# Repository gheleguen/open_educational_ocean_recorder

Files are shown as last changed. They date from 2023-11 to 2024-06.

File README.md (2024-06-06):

# Sonde de température de fond
## 1/ Introduction
Cette sonde est un instrument permettant d'enregistrer la température de fond marin avec un précision de l'ordre du dixième de degrés Celsius. 
Elle a été conçu pour permettre un simple enregistrement de la température de l'eau en fonction du temps. 
La sonde est disigné de manière à pouvoir recevoir de nouvelles fonctions comme la mesure de la pression ou de la conductivité. 

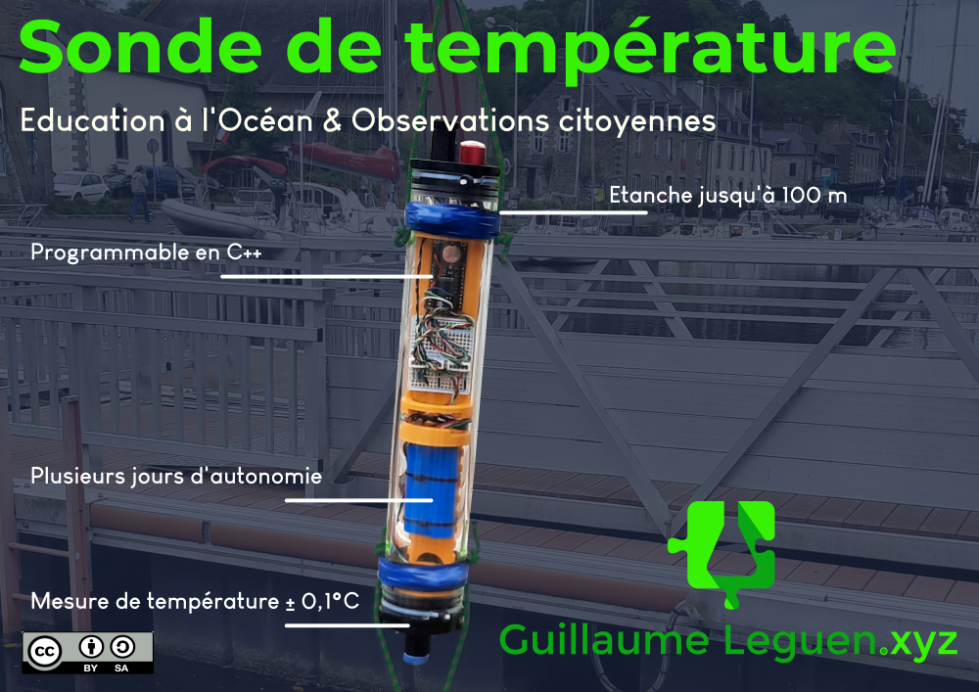
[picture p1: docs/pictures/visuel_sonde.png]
Visuel sonde de température


## 2/ Toutes les clés pour se lancer

### 2.1 Télécharger l'archive

Avant toute chose, [télécharger l'archive du projet](https://github.com/gheleguen/open_educational_ocean_recorder/archive/refs/heads/main.zip). C'est dans ce dossier que se trouve tous les fichiers de documentations mais aussi les fichiers de découpes ou les modèles d'impression 3D. 

**Ou passer par Git Hub**

Se rendre dans le [git hub](https://github.com/gheleguen/open_educational_ocean_recorder.git) et télécharger l'archive complète du projet. 

**Ou en lignes de commandes**

 - Ouvrir un terminal linux,
 - Si ce n'est pas déjà fait installer ```git``` : <pre>sudo apt install git</pre>
 - Se placer dans le dossier de votre ordinateur où vous souhaitez enregistrer l'archive.
 - Cloner l'archive : <pre>git clone https://github.com/gheleguen/open_educational_ocean_recorder.git</pre> 

### 2.2 L'arborescence de l'archive

 - **docs :** Est le dossier qui contient les documents et images qui constituent la documentation.  Ce sont des fichiers marckdown (.md) que l'on peut ouvrir avec un éditeur de texte.

 - **Hardware :** Le dossier qui contient les fichiers d'impressions 3D, de découpe laser...  

 - **Software :** Le dossier qui contient le code à flasher sur l'arduino.

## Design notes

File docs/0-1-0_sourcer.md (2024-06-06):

# A. Nomenclature / Le sourcing (V1.0)

Le sourcing est la première étape du projet et souvent la plus fastidieuse. Sourcer désigne le fait de rassembler tout ce qui sera nécéssaire pour fabriquer un objet libre. Ce projet demande des composants que l'on trouvera chez un grand-nombre de fournisseurs différents. De plus, ces fournisseurs peuvent différer en fonction du lieu et du moment où l'on va construire un instrument.

**Attention :** Veiller à effectuer ce travail préparatoire bien avant la fabrication. En effet, certaines commandes peuvent avoir de long délais. Et cela sans compter le temps nécessaire pour le travail du sourcing lui-même. 

## 1. Présentation du fichier de sourcing

 - Chercher dans le dossier "docs/files/sourcing" directement dans l'archive github, le tableur qui conviendrait à votre région ou plus proche en temps de votre date d'achat. 
 - Ouvrir le fichier de sourcing au moyen d'un tableur. Ce fichier a été créé au moyen du logiciel libre [Libre office calc](https://fr.libreoffice.org/download/telecharger-libreoffice/) mais pourra très bien être ouvert par d'autres logiciels de tableurs.

 - Ce fichier se compose d'un onglet listant tous les composants et plusieurs autres onglets dont chacun permettra au moyen d'un tableau croisé dynamique de réaliser des notes de traçabilités (ceci permettra de faciliter le travail de validation par votre administration avant l'achat):

### 1.1 Détails du tableau "Liste des éléments"

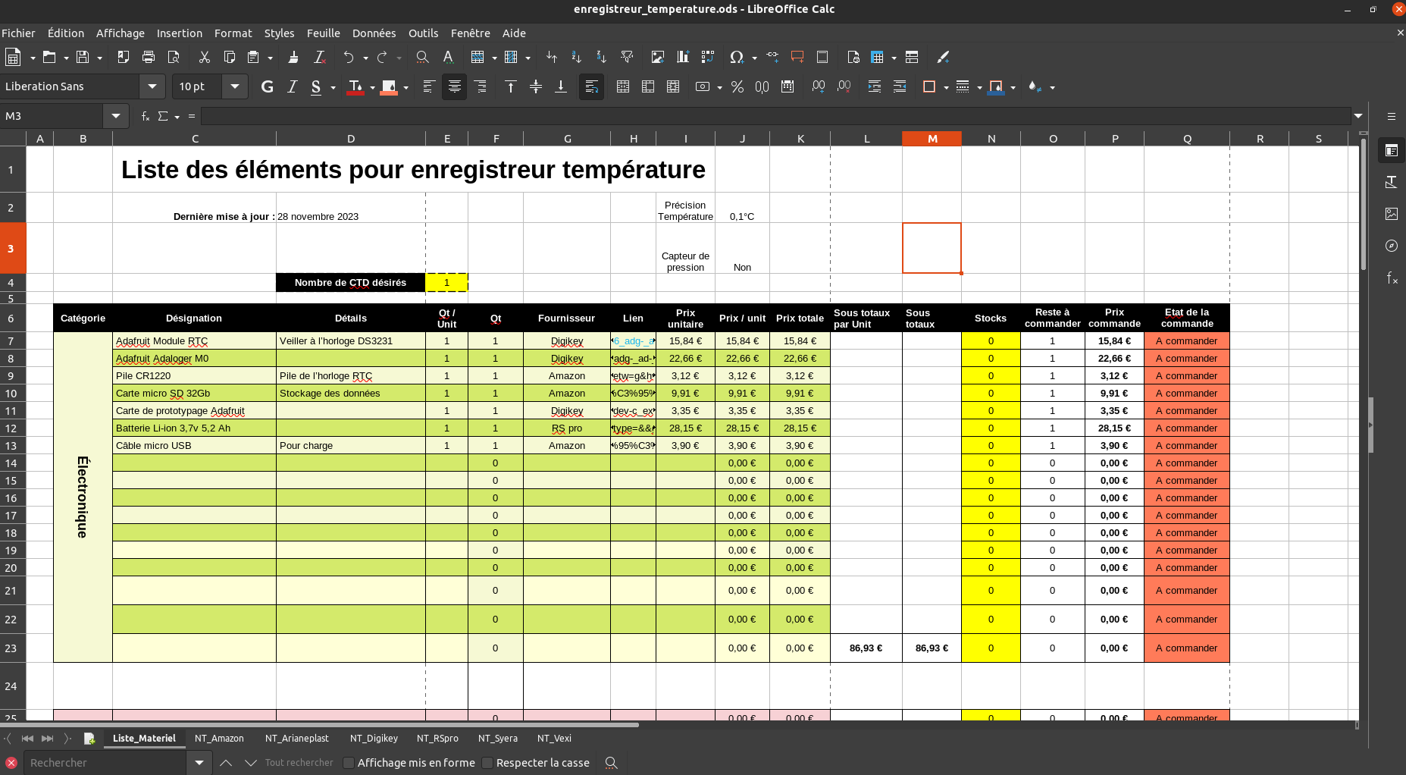
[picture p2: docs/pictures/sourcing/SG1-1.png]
SG1-1


 - **Catégorie :** Catégorie de composants (ex : Electronique, Visserie...)
 - **Désignation :** Appellation du composant
 - **Détails :** Information complémentaire, souvent des détails auquel faire attention.
 - **Qt / Unité :** Quantité pour un instrument,
 - **Qt :** Quantité nécessaire totale pour tous les instrument que l'on souhaite fabriquer,
 - **Fournisseur :** Nom du fournisseur,
 - **Lien :** Lien d'achat,
 - **Prix unitaire :** Prix d'un seul composant,
 - **Prix / Unit :** Prix des composants de même nom pour un seul instrument,
 - **Prix totale :** Prix des composants de même nom pour tous les instruments que l'on souhaite fabriquer,
 - **Stocks :** Nombre de pièces déjà en stock,
 - **Reste à commander :** Nombre de pièces qu'il reste à commander,
 - **Prix commande :** Prix total de chacun des groupes de composants qu'il reste à commander,
 - **Etat de la commande :** Cette colonne permet de sélectionner l'état de l'approvisionnement pour chacun des composant listé. Il existe 4 états : "A commander", "En attente de réception", "Reçu" et "Colis perdu"

### 1.2 Détails d'une table "note de traçabilité"

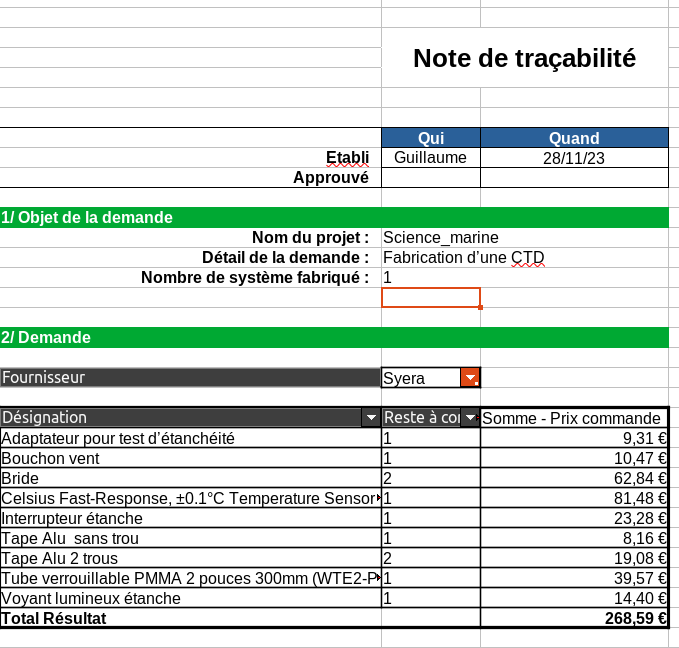
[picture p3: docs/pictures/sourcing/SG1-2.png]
SG1-2


 - Dans la seconde partie on pourra modifier au moyen d'un menu déroulant le nom du fournisseur. 
 - Le nombre de composants et les prix affichés correspondent aux quantités après déduction du stock (cf. 1.1 Détails...)
 - Noter que si la valeur renseignée dans la colonne "stocks" de la table "Liste_Materiel" est supérieure ou égale à la quantité totale nécéssaire, la quantité restante à acheter sera de 0. 

## 2. Utilisation du tableur pour sourcer

### 2.1 Mettre à jour les informations des composants

 - Se rendre dans l'onglet "Liste_Matériel"
 - Toutes les cases colorés en jaune sont à éditer en priorité : Changer le nombre d'instruments désirés et remplir la colonne des stocks (colonne"N"). Renseigner "0" si aucun composant en stock.
 - Consulter chaque lien un par un (colonne"H"), vérifier que le fournisseur convient, que le prix unitaire correspond bien à celui indiqué dans le tableau. Dans le cas contraire modifier la valeur dans la colonne "I".
 - Si le fournisseur ne distribue plus ce composant, ou que le fournisseur ne convient pas, chercher le composant ailleurs puis mettre à jour les colonnes "G" "H" et "I" avec les informations du nouveau fournisseur.
 - Surveiller ainsi ces éléments pour chacune des lignes de l'onglet "Liste_Materiel".

### 2.2 Actualiser les notes de traçabilités

 - Éditer l'entête et la partie "1/" comme désiré,
 - Pour mettre à jour la table croisée, cliquer droit sur "fournisseur" puis "actualiser",
 - Créer un onglet pour chaque fournisseur listé. 

## 3. Contribuer

Dans le cas où vous avez modifié le tableur avec des fournisseurs différents ce due au fait que vous ne résidez pas dans la même région ou pour toute autre raison, vos informations pourraient bénéficier par la suite à d'autres personnes.

**Pour contribuer**, déposez votre fichier dans le git à l'emplacement suivant "docs/files/sourcing"

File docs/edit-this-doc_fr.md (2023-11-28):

# Éditer cette documentation

## 1/ Introduction
|||
|-|-|
|Cette documentation est mise en page par ReadTheDocs.org et [lisible à l'adresse ci attaché](https://porte-a-poules.readthedocs.io/fr/latest/). En aucun cas, cette adresse permet d'éditer la documentation.|ED1-1|
|Afin de pouvoir contribuer à cette documentation, vous pouvez contribuer directement au [repository GitHub](https://github.com/gheleguen/porte_a_poules).|ED1-2|

C'est sur GitHub que sont déposés les fichiers sources. On y retrouve l'arborescence suivante : 

 - **docs :** Est le dossier qui contient les documents qui pourront être affichés sur le read the doc. Dans ce dossier sont entreposés :

   - A la racine les fichiers marckdown qui sont les textes de la documentation. Pour chaque onglet sur read the doc nous ajouterons un fichier séparé avec un titre en Anglais sans espaces terminé par "_fr" pour la version française ou "_en" pour le version anglaise. L'extention sera toujours ".md".
   - Le dossier "pictures" : Qui contient plusieurs dossiers dont chacun porte un nom en rapport avec le fichier marckdown auquel il se rapporte. Ainsi pour un fichier de doccumentation "test1_fr.md" on prendra le soin d'entreposer les images dans un dossier "/docs/pictures/test1".

 - **Hardware :** Qui est le dossier qui contient les fichiers d'impressions 3D, de découpe laser...  

Avant de faire une proposition de contribution, il est bienvenue d'éditer le repository depuis votre compte en effectuant un forke de la présente documentation. Une fois que vous aurez une version prête à être publiée il suffira de faire une pull request au "main project".
C'est un administrateur qui étudiera votre proposition pour en intégrer tout ou partie sur le projet. 

## 2/ Édition (généralités)
Ces actions peuvent se réaliser directement sur la plateforme gilhub.

### 2.1 Écriture en Marckdown
Le Marckdown est un langage de mise en forme de texte très simplifié. On peut éditer un fichier ".md" directement via gitHub ou en local de son ordinateur avec n'importe quel éditeur de texte. Cependant nous recommandons [Ghostwriter](https://ghostwriter.kde.org/fr/) qui présente l'avantage de proposer une vue en direct du rendu (aperçu HTML).

[Pour ce qui est de la syntaxe, consulter ce guide](https://www.markdownguide.org/basic-syntax/)

### 2.2 Ajout et mise à jour d'une image

#### 2.2.1 Ajout
Les images que l'on souhaite faire apparaître dans la documentation ne doivent pas être collées dans le document. 

 - Importer les images désirées que l'on aura préalablement réduites en taille chacune en dessous de 200Ko et renommées de manière à être facilement identifiables. 
 - Dans le fichier de documentation corespondant à la ligne où l'on souhaite faire apparaître l'image, ajouter la ligne suivante : 
 ```Legende_Image``` 

#### 2.2.2 Mise à jour 
Pour mettre à jour une image, il suffit de supprimer du git l'image en question et d'uploader la nouvelle image en prenant soin de renommer cette nouvelle image avec le nom exact de l'ancienne. 

## 3/ Édition du dépôt en locale (Intermédiaire)
Cette méthode permet de cloner l'archive disponible sur github sur un disque dure. Ainsi on pourra facilement modifier les différents fichiers mais aussi l'arborescence sans nécéssiter de connexion internet mais surtout cela va permettre de préparer une version qui pourra par la suite faire l'objet d'un pull request. 
Toute la démarche décrite ci-dessous est valable uniquement pour un usage depuis un ordinateur sous Linux. Il existe nécessairement des équivalent pour les autres OS mais les lignes de commandes restent les même.

### 2.1 Installer Git et préparer le terrain
 - Sur votre disque dure, définir l'espace où sera stocké le dépôt. Sachez qu'un dépôt GitHub peut peser jusq'à 500Mo. De préférence définir un dossier vide. **Attention* A ce qu'aucun dossier ou sous-dossier du chemin ne comporte de caractères spéciaux ou d'espaces. Remplacer tous les espaces par des underscore "_". 
 - Ouvrir un terminal (*Ctrl + Alt + t* sur Unbuntu).
 - Dans le cas où le paquet "git" n'est pas déjà installé sur votre PC, lancez l'installation de git :  ```sudo apt install git``` (Cette action nécessite une connexion internet).

### 2.2 Cloner le dépôt sur son disque dure
 - Ouvrir une page web avec le github que l'on souhaite cloner
 - Y copier le code "https" que l'on trouvera dans l'onglet déroulant "code" en haut à droite.
 - Dans un terminal se diriger vers l'espace prévu pour coller le dépôt. Utiliser la commande ```cd puis_chemin/de_votre_dossier```
 - Cloner le dépôt git en utilisant la commande ```git clone https://github.com/identifiant/nom_du_projet.git``` Prendre soin de remplacer l'url par celui du dépôt désiré si il est différent du notre. 
 - Le clonage va prendre quelques minutes et va coller tous les fichiers et l'arborescence dans votre répertoire.

### 2.3 Modifier le dépôt
 - Sur votre poste de travail, modifiez tous les fichiers nécessaires, déposer des fichiers, suprimez en...
 - Avant de commencer à travailler peut-être que le dépôt en ligne a été modifié depuis votre dernière mise à jour. Pour mettre à jour votre dépôt en local. Se positionner tout d'abord dans le dépôt ```cd NomduDepot``` Puis effectuer un "Pull" ```git pull```
 
### 2.4 Proposer des modifications
Si vous avez effectué des modifications, il peut-être utile de les proposer en modification au projet. Mais avant cela il peut-être utile de créer une nouvelle branche ou de faire cela depuis votre fork. 
 - Pour ajouter l'ensemble des fichiers à la liste des fichiers à commiter : ```git add *```
 - Commiter ```git commit -m "commentaire associé au commit" git@git.cru.fr:nom_projet.git nom_branche (par défaut master représentant la branche principale)```
 - Enfin pousser votre travail ```git push```

## Liens connexes
 - [Documentation Git](https://git-scm.com/about)
 - [Formation vidéo à Git](https://youtube.com/playlist?list=PLjwdMgw5TTLXuY5i7RW0QqGdW0NZntqiP)

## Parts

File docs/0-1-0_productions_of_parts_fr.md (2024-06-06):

# B. Préparation des pièces (v1.0)
## 1/ Impression des pièces en 3D

Imprimer toutes les pièces nécessaires en veillant à respecter les recommandations de remplissage des pièces extérieurs. 
 - [Les fichiers STL sont disponibles ici](https://github.com/gheleguen/open_educational_ocean_recorder/hardware/v0-1-0) .

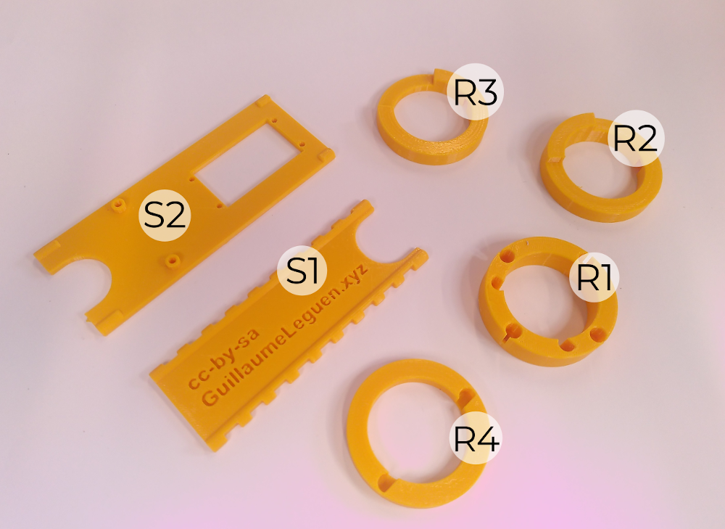
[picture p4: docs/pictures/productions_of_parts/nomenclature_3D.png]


**1.1 Pour l'intérieur du caisson :**

Il n'y a pas d'obligation quand au matériau d'impression de ces pièces. Le PET est le matériau que nous avons utilisé du fait qu’il est très facilement accessible dans le commerce. Le PLA parait à écarter tant parfois il arrive au à la sonde d'être stocké au soleil. La température si elle atteint 60° pourrait déformer des pièces en PLA. 

Le remplissage pourra être alvéolé de manière à économiser de la matière. Nous utilisons régulièrement un remplissage à 20% et une résolution de 0,2mm.

|    Visuel    |Référence|Quantité|Dénomination et usage|
|------------------------------------|------|------|-----------------|
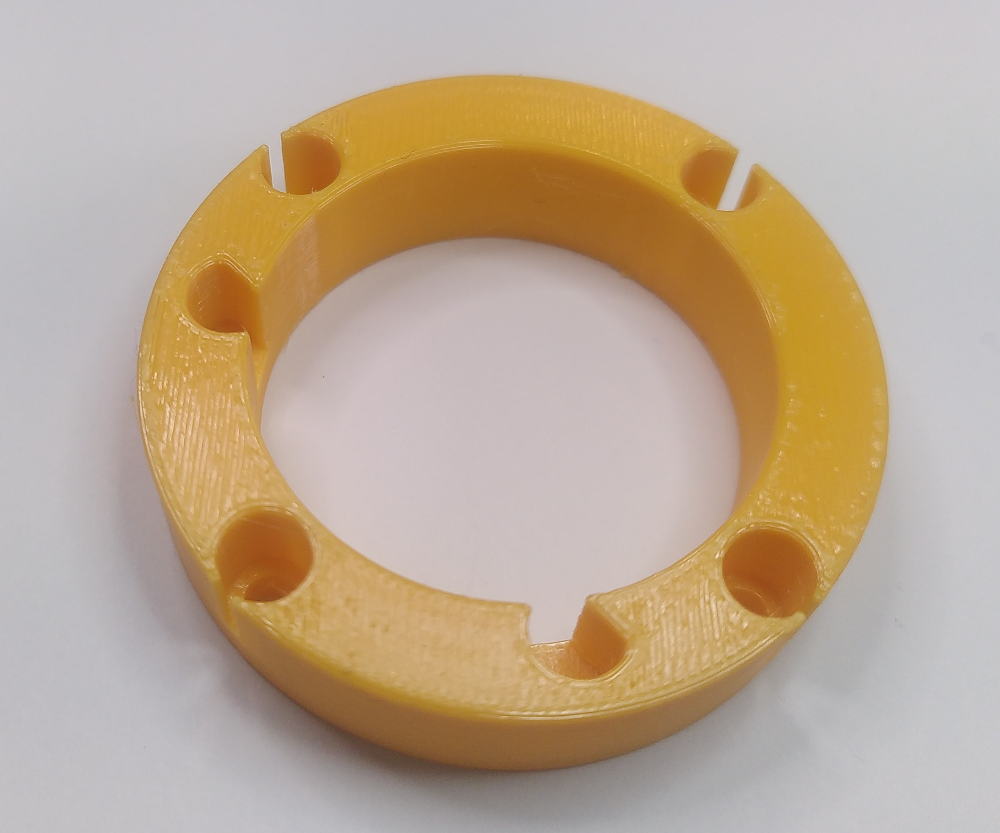
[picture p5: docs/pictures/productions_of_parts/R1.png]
POP1-1-I1
||[R1](https://github.com/gheleguen/open_educational_ocean_recorder/blob/main/hardware/v0-1-0/R1.stl)|1|Rondelle permettant de visser le support de batterie à la bride basse.|
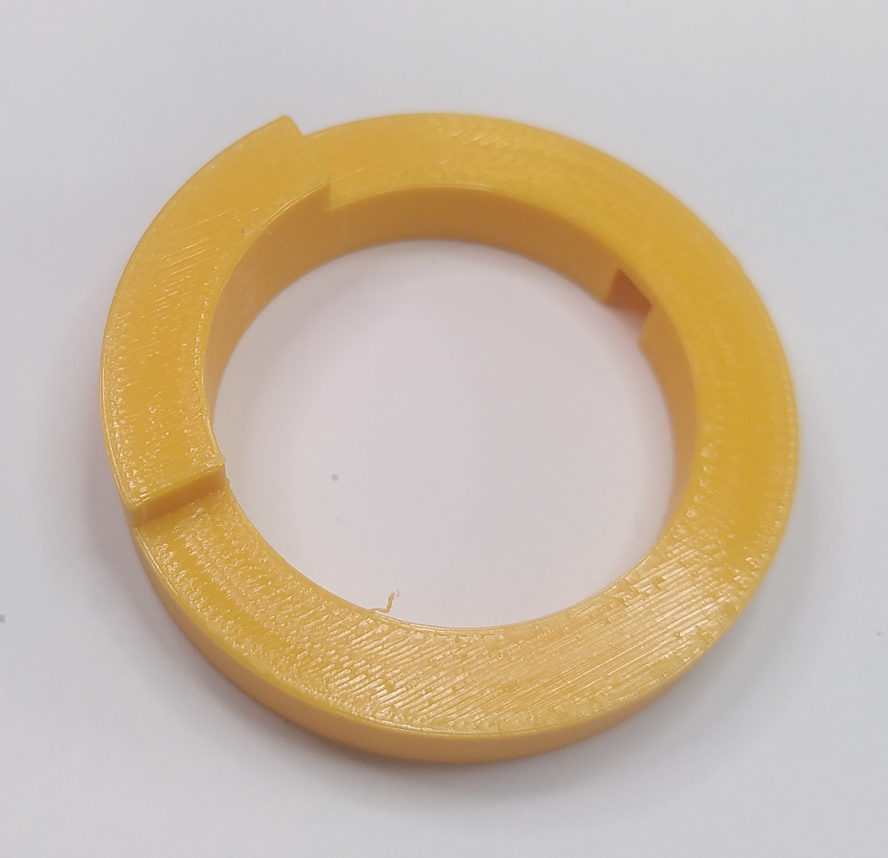
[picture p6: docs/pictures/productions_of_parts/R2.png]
POP1-1-I2
||[R2](https://github.com/gheleguen/open_educational_ocean_recorder/blob/main/hardware/v0-1-0/R2.stl)|1|Baggue haute du support de batterie. Elle est constitué d'un créneau permettant de s'imbriquer dans le support de carte électronique.|
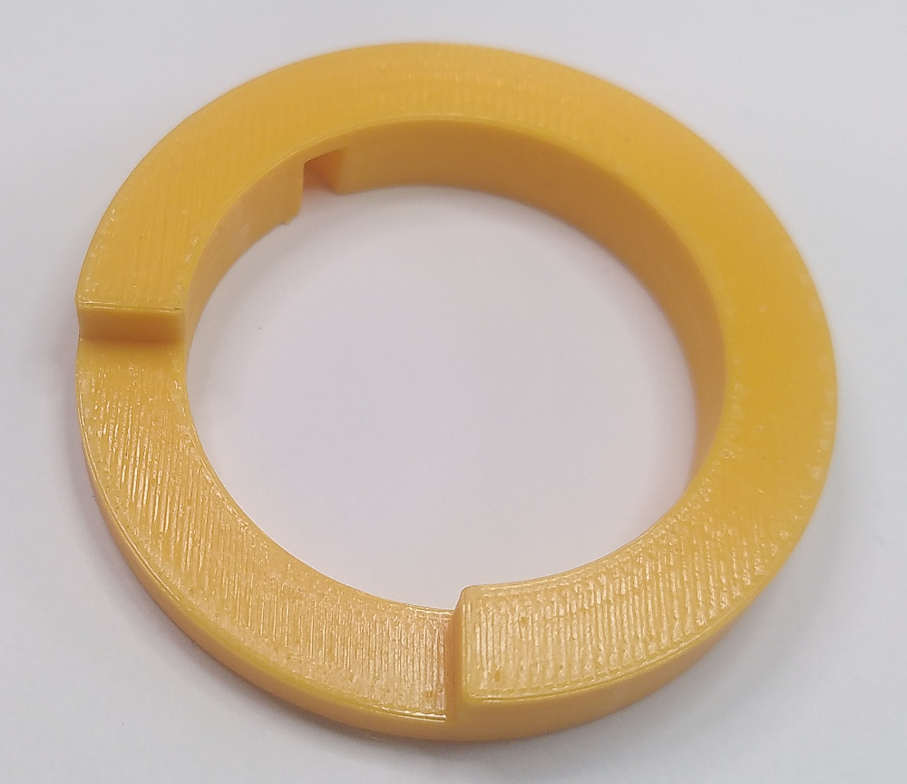
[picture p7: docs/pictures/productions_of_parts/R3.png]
POP1-1-I3
||[R3](https://github.com/gheleguen/open_educational_ocean_recorder/blob/main/hardware/v0-1-0/R3.stl)|1|Bague basse de support de carte électronique. Un creux permet de bloquer l'angle avec le support de batterie.|
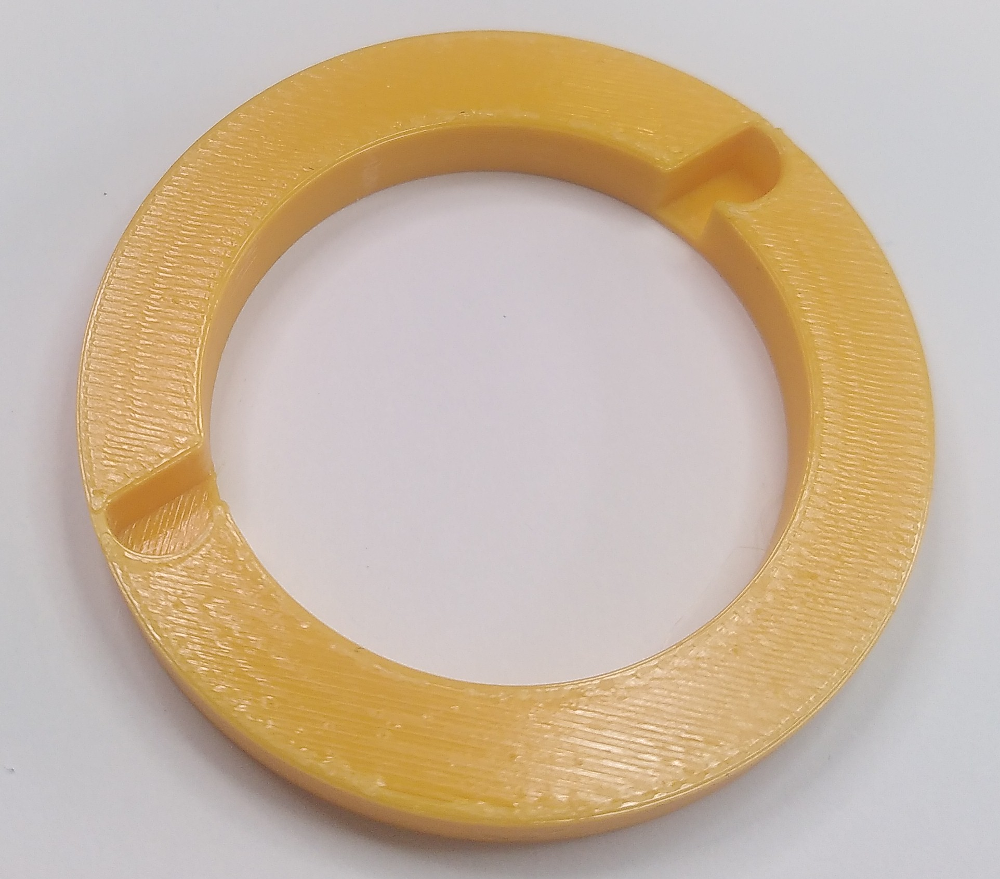
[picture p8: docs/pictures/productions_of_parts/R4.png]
||[R4](https://github.com/gheleguen/open_educational_ocean_recorder/blob/main/hardware/v0-1-0/R4.stl)|1|Bague du haut de la sonde au dessus du support des cartes électroniques|
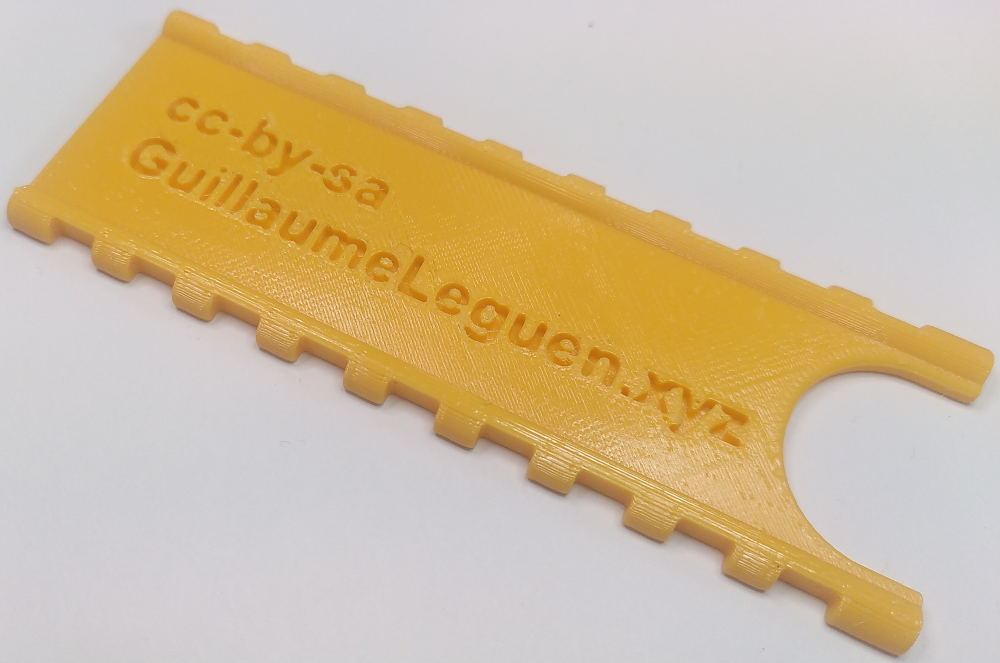
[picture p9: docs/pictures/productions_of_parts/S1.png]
||[S1](https://github.com/gheleguen/open_educational_ocean_recorder/blob/main/hardware/v0-1-0/S1.stl)|1|Support de batterie. Les créneaux permettent de fixer les batteries au moyen de colliers de serrages.|
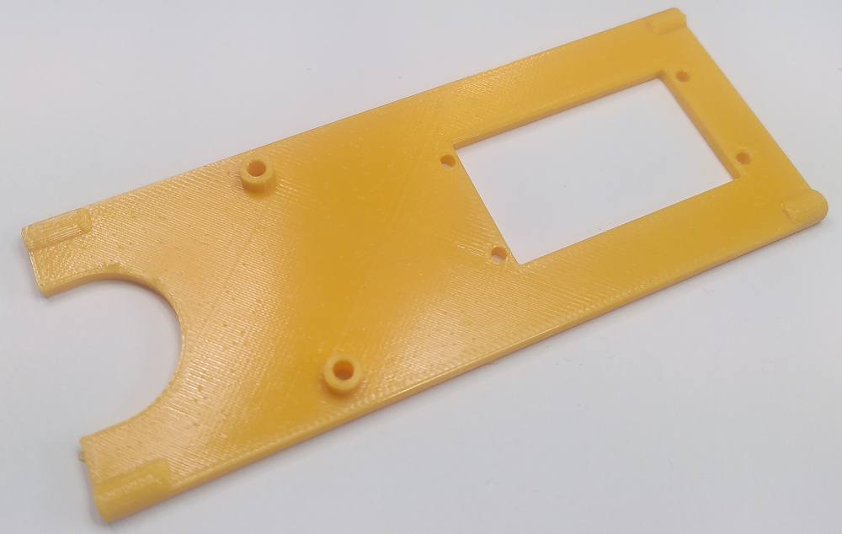
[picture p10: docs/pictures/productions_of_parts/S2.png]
||[S2](https://github.com/gheleguen/open_educational_ocean_recorder/blob/main/hardware/v0-1-0/S2.stl)|1|Support des cartes électroniques.|

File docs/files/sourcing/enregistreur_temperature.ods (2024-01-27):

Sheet: Liste_Materiel
 | Liste des éléments pour enregistreur température
 | Dernière mise à jour : | 27 janvier 2024 |  |  |  |  | Précision Température | 0,1°C
 |  |  |  |  |  |  | Capteur de pression | Non
 |  | Nombre de CTD désirés | 2
Catégorie | Désignation | Détails | Qt / Unit | Qt | Fournisseur | Lien | Prix unitaire | Prix / unit | Prix totale | Sous totaux par Unit | Sous totaux | Stocks | Reste à commander | Prix commande | Etat de la commande | Commentaire
Électronique | Adafruit Module RTC | Veiller à l’horloge DS3231 | 1 | 2 | Digikey | https://www.digikey.fr/fr/products/detail/adafruit-industries-llc/3028/5885910?productid=5885910&gad_source=1 | 15,31 € | 15,31 € | 30,62 € |  |  | 0 | 2 | 30,62 € | A commander
 | Adafruit Adaloger M0 |  | 1 | 2 | Digikey | https://www.digikey.fr/fr/products/detail/adafruit-industries-llc/2796/5804105?productid=5804105&gad_source=1 | 21,90 € | 21,90 € | 43,80 € |  |  | 0 | 2 | 43,80 € | A commander
 | Pile CR1220 | Pile de l’horloge RTC | 1 | 2 | Amazon | https://www.amazon.fr/Direct-Duracell-lithium-emball%C3%A9es-blister/dp/B005OQJCQI?adgrpid=53681020742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 | 3,12 € | 3,12 € | 6,24 € |  |  | 0 | 2 | 6,24 € | A commander
 | Carte micro SD 32Gb | Stockage des données | 1 | 2 | Amazon | https://www.amazon.fr/SANDISK-Ultra-32-SDHC-MEM/dp/B08KSY222G?__mk_fr_FR=%C3%85M%C3%85%C5%BD%C3%95%C3%91 | 6,75 € | 6,75 € | 13,50 € |  |  | 0 | 2 | 13,50 € | A commander
 | Carte de prototypage Adafruit |  | 1 | 2 | Digikey | https://www.digikey.fr/fr/products/detail/adafruit-industries-llc/1608/5154676?productid=5154676&gad_source=1 | 3,24 € | 3,24 € | 6,48 € |  |  | 0 | 2 | 6,48 € | A commander
 | Batterie Li-ion 3,7v 5,2 Ah |  | 1 | 2 | RS pro | https://fr.rs-online.com/web/p/blocs-batteries-rechargeables/1449407?matchtype=&gad_source=1&gclsrc=aw.ds | 28,15 € | 28,15 € | 56,30 € |  |  | 0 | 2 | 56,30 € | A commander
 | Câble micro USB | Pour charge | 1 | 2 | Amazon | https://www.amazon.fr/transfert-donn%C3%A9es-chargement-dappareils-compatibles/dp/B08YZ23C66?__mk_fr_FR=%C3%85M%C3%85%C5%BD%C3%95%C3%91 | 3,90 € | 3,90 € | 7,80 € |  |  | 0 | 2 | 7,80 € | A commander
 |  |  |  | 0 |  |  |  | 0,00 € | 0,00 € |  |  | 0 | 0 | 0,00 € | A commander
 |  |  |  | 0 |  |  |  | 0,00 € | 0,00 € |  |  | 0 | 0 | 0,00 € | A commander
 |  |  |  | 0 |  |  |  | 0,00 € | 0,00 € |  |  | 0 | 0 | 0,00 € | A commander
 |  |  |  | 0 |  |  |  | 0,00 € | 0,00 € |  |  | 0 | 0 | 0,00 € | A commander
 |  |  |  | 0 |  |  |  | 0,00 € | 0,00 € |  |  | 0 | 0 | 0,00 € | A commander
 |  |  |  | 0 |  |  |  | 0,00 € | 0,00 € |  |  | 0 | 0 | 0,00 € | A commander
 |  |  |  | 0 |  |  |  | 0,00 € | 0,00 € |  |  | 0 | 0 | 0,00 € | A commander
 |  |  |  | 0 |  |  |  | 0,00 € | 0,00 € |  |  | 0 | 0 | 0,00 € | A commander
 |  |  |  | 0 |  |  |  | 0,00 € | 0,00 € |  |  | 0 | 0 | 0,00 € | A commander
 |  |  |  | 0 |  |  |  | 0,00 € | 0,00 € | 82,37 € | 164,74 € | 0 | 0 | 0,00 € | A commander
Capteurs |  |  |  | 0 |  |  |  | 0,00 € | 0,00 € |  |  | 0 | 0 | 0,00 € | A commander
 | Celsius Fast-Response, ±0.1°C Temperature Sensor (I2C) |  | 1 | 2 | Syera | http://syera.fr/boutique/fr/pression-temperature/278-capteur-de-temperature.html | 81,48 € | 81,48 € | 162,96 € |  |  | 0 | 2 | 162,96 € | A commander
 |  |  |  | 0 |  |  |  | 0,00 € | 0,00 € |  |  | 0 | 0 | 0,00 € | A commander
 |  |  |  | 0 |  |  |  | 0,00 € | 0,00 € |  |  | 0 | 0 | 0,00 € | A commander
 |  |  |  | 0 |  |  |  | 0,00 € | 0,00 € | 81,48 € | 162,96 € | 0 | 0 | 0,00 € | A commander
Etanchéité | Tube verrouillable PMMA 2 pouces 300mm (WTE2-P-LOCK-TUBE-300-R1) |  | 1 | 2 | Syera | http://syera.fr/boutique/fr/tubes-2-pouces/138-tube-verrouillable-pmma-2-pouces-300mm.html | 39,57 € | 39,57 € | 79,14 € |  |  | 0 | 2 | 79,14 € | A commander
 | Bouchon vent |  | 1 | 2 | Syera | http://syera.fr/boutique/fr/accessoires-outillage/248-mise-a-l-air-libre.html?search_query=bouchon&results=48 | 10,47 € | 10,47 € | 20,94 € |  |  | 0 | 2 | 20,94 € | A commander
 | Bouchon verrouillable, aluminium 2 trous |  | 2 | 4 | Syera | http://syera.fr/boutique/fr/brides-tapes-hublots-et-domes-2-pouces/132-bouchon-verrouillable-2-trous-pour-tube-2-pouces.html?search_query=bouchon&results=48 | 37,24 € | 74,48 € | 148,96 € |  |  | 0 | 4 | 148,96 € | A commander
 | Voyant lumineux étanche |  | 1 | 2 | Syera | http://syera.fr/boutique/fr/eclairages-voyants-lasers/53-voyant-etanche-vert.html?search_query=pompe+a+vide&results=24 | 14,40 € | 14,40 € | 28,80 € |  |  | 0 | 2 | 28,80 € | A commander
 | Interrupteur étanche |  | 1 | 2 | Syera | http://syera.fr/boutique/fr/accessoires-outillage/273-interrupteur-etanche-m10-5a.html | 23,28 € | 23,28 € | 46,56 € | 162,20 € | 324,40 € | 0 | 2 | 46,56 € | A commander
Autres (*1 par groupe d’instruments) | Kit GPIO header |  | 1 | 1 | Amazon | https://www.amazon.fr/Femelle-Connecteur-Breakaway-Arduino-Prototype/dp/B093LBN495?__mk_fr_FR=%C3%85M%C3%85%C5%BD%C3%95%C3%91&sp_csd=d2lkZ2V0TmFtZT1zcF9tdGY | 13,99 € | 13,99 € | 13,99 € |  |  | 0 | 1 | 13,99 € | A commander
 | Pompe à vide | Pompe pour tester l’étanchéité des instruments | 1 | 1 | Amazon | https://www.amazon.fr/Awsuc-Manuelle-Purgeur-adaptateurs-Diagnostic/dp/B09MN36PZF?__mk_fr_FR=%C3%85M%C3%85%C5%BD%C3%95%C3%91 | 18,92 € | 18,92 € | 18,92 € |  |  | 0 | 1 | 18,92 € | A commander
 | Adaptateur pour test d’étanchéité |  | 1 | 1 | Syera | http://syera.fr/boutique/fr/accessoires-outillage/246-prise-pour-test-d-etancheite.html | 9,31 € | 9,31 € | 9,31 € |  |  | 0 | 1 | 9,31 € | A commander
 | Graisse silicone | Pour étanchéité | 1 | 1 | Amazon | https://www.amazon.fr/Xavax-Graisse-silicone-multiple-1110/dp/B00APYQTPQ?__mk_fr_FR=%C3%85M%C3%85%C5%BD%C3%95%C3%91 | 12,99 € | 12,99 € | 12,99 € |  |  | 0 | 1 | 12,99 € | A commander
 | Connectiques JST | Avec pince | 1 | 1 | Amazon | https://www.amazon.fr/connecteurs-PEBA-femelle-Adaptateur-Connecteur/dp/B07VW8F1NB?__mk_fr_FR=%C3%85M%C3%85%C5%BD%C3%95%C3%91 | 38,99 € | 38,99 € | 38,99 € |  |  | 0 | 1 | 38,99 € | A commander
 | Fils pour connectiques |  | 1 | 1 | Amazon | https://www.amazon.fr/Aussel-couleur-darc-en-ciel-1-27mm-connecteurs/dp/B077XF5LXH | 12,28 € | 12,28 € | 12,28 € |  |  | 0 | 1 | 12,28 € | A commander
 | Valise de transport H125 | /!\ Attention prendre la valise avec la mousse pré-découpé ! Valise etanche pouvant contenir 5 sondes | 1 | 1 | Vexi | https://www.vexi.fr/details/valises-plastique/etanches/valise-465-h125/ | 88,01 € | 88,01 € | 88,01 € |  |  | 0 | 1 | 88,01 € | A commander
 | Filament pour impression 3D | Choisir du PETG couleur au choix (sans copeaux de métaux) | 1 | 1 | Arianeplast | https://www.arianeplast.com/218-3d-filament-petg | 24,00 € | 24,00 € | 24,00 € | 218,49 € | 218,49 € | 0 | 1 | 24,00 € | A commander
Frais de ports | Frais de port Amazon |  | 1 | 1 | Amazon |  | 8,00 € | 8,00 € | 8,00 € |  |  | 0 | 1 | 8,00 €
 | Frais de port Arianeplast |  | 1 | 1 | Arianeplast |  | 7,00 € | 7,00 € | 7,00 € |  |  | 0 | 1 | 7,00 €
 | Frais de port Vexi |  | 1 | 1 | Vexi |  | 9,80 € | 9,80 € | 9,80 € |  |  | 0 | 1 | 9,80 €
 | Frais de port Digikey |  | 1 | 1 | Digikey |  | 18,00 € | 18,00 € | 18,00 € |  |  | 0 | 1 | 18,00 €
 | Frais de port Rspro |  | 1 | 1 | RS pro |  | 8,50 € | 8,50 € | 8,50 € |  |  | 0 | 1 | 8,50 €
 | Frais de port Syera |  | 1 | 1 | Syera |  | 11,82 € | 11,82 € | 11,82 € |  |  | 0 | 1 | 11,82 €
 |  |  |  | 1 |  |  |  | 0,00 € | 0,00 € |  |  | 0 | 1 | 0,00 €
 |  |  |  | 1 |  |  |  | 0,00 € | 0,00 € |  |  | 0 | 1 | 0,00 €
 |  |  |  | 1 |  |  |  | 0,00 € | 0,00 € |  |  | 0 | 1 | 0,00 €
 |  |  |  | 1 |  |  |  | 0,00 € | 0,00 € |  |  | 0 | 1 | 0,00 €
 |  |  |  | 1 |  |  |  | 0,00 € | 0,00 € |  |  | 0 | 1 | 0,00 €
 |  |  |  | 1 |  |  |  | 0,00 € | 0,00 € | 63,12 € | 63,12 € | 0 | 1 | 0,00 €
 |  |  |  |  |  |  |  | Total (Hors frais de ports) |  |  | 870,59 €
 |  |  |  |  |  |  |  | Total (TTC) |  |  | 933,71 € | Totale des commandes |  | 933,71 €
 |  |  |  |  | Etat
 |  |  |  |  | A commander
 |  |  |  |  | En attente de réception
 |  |  |  |  | Reçu
 |  |  |  |  | Colis perdu
 |  |  |  |  | Rien

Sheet: NT_Amazon
 | Note de traçabilité
 | Qui | Quand
Etabli |  | 27/01/24
Approuvé
1/ Objet de la demande
Nom du projet : | Science_marine
Détail de la demande : | Fabrication d’une CTD
Nombre de système fabriqué : | 2
2/ Demande
Fournisseur | Amazon
Désignation | Reste à commander | Somme - Prix commande
Câble micro USB | 2 | 7,80 €
Carte micro SD 32Gb | 2 | 13,50 €
Connectiques JST | 1 | 38,99 €
Fils pour connectiques | 1 | 12,28 €
Frais de port Amazon | 1 | 8,00 €
Graisse silicone | 1 | 12,99 €
Kit GPIO header | 1 | 13,99 €
Pile CR1220 | 2 | 6,24 €
Pompe à vide | 1 | 18,92 €
Total Résultat |  | 132,71 €

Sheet: NT_Arianeplast
 | Note de traçabilité
 | Qui | Quand
Etabli |  | 27/01/24
Approuvé
1/ Objet de la demande
Nom du projet : | Science_marine
Détail de la demande : | Fabrication d’une CTD
Nombre de système fabriqué : | 2
2/ Demande
Fournisseur | Arianeplast
Désignation | Reste à commander | Somme - Prix commande
Filament pour impression 3D | 1 | 24,00 €
Frais de port Arianeplast | 1 | 7,00 €
Total Résultat |  | 31,00 €

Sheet: NT_Digikey
 | Note de traçabilité
 | Qui | Quand
Etabli |  | 27/01/24
Approuvé
1/ Objet de la demande
Nom du projet : | Science_marine
Détail de la demande : | Fabrication d’une CTD
Nombre de système fabriqué : | 1
2/ Demande
Fournisseur | Digikey
Désignation | Reste à commander | Somme - Prix commande
Adafruit Adaloger M0 | 2 | 43,80 €
Adafruit Module RTC | 2 | 30,62 €
Carte de prototypage Adafruit | 2 | 6,48 €
Frais de port Digikey | 1 | 18,00 €
Total Résultat |  | 98,90 €

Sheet: NT_RSpro
 | Note de traçabilité
 | Qui | Quand
Etabli | Guillaume | 27/01/24
Approuvé
1/ Objet de la demande
Nom du projet : | Science_marine
Détail de la demande : | Fabrication d’une CTD
Nombre de système fabriqué : | 2
2/ Demande
Fournisseur | RS pro
Désignation | Reste à commander | Somme - Prix commande
Batterie Li-ion 3,7v 5,2 Ah | 2 | 56,30 €
Frais de port Rspro | 1 | 8,50 €
Total Résultat |  | 64,80 €

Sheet: NT_Syera
 | Note de traçabilité
 | Qui | Quand
Etabli | Guillaume | 27/01/24
Approuvé
1/ Objet de la demande
Nom du projet : | Science_marine
Détail de la demande : | Fabrication d’une CTD
Nombre de système fabriqué : | 2
2/ Demande
Fournisseur | Syera
Désignation | Reste à commander | Somme - Prix commande
Adaptateur pour test d’étanchéité | 1 | 9,31 €
Bouchon vent | 2 | 20,94 €
Bouchon verrouillable, aluminium 2 trous | 4 | 148,96 €
Celsius Fast-Response, ±0.1°C Temperature Sensor (I2C) | 2 | 162,96 €
Frais de port Syera | 1 | 11,82 €
Interrupteur étanche | 2 | 46,56 €
Tube verrouillable PMMA 2 pouces 300mm (WTE2-P-LOCK-TUBE-300-R1) | 2 | 79,14 €
Voyant lumineux étanche | 2 | 28,80 €
Total Résultat |  | 508,49 €

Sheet: NT_Vexi
 | Note de traçabilité
 | Qui | Quand
Etabli | Guillaume | 27/01/24
Approuvé
1/ Objet de la demande
Nom du projet : | Science_marine
Détail de la demande : | Fabrication d’une CTD
Nombre de système fabriqué : | 2
2/ Demande
Fournisseur | Vexi
Désignation | Reste à commander | Somme - Prix commande
Frais de port Vexi | 1 | 9,80 €
Valise de transport H125 | 1 | 88,01 €
Total Résultat |  | 97,81 €

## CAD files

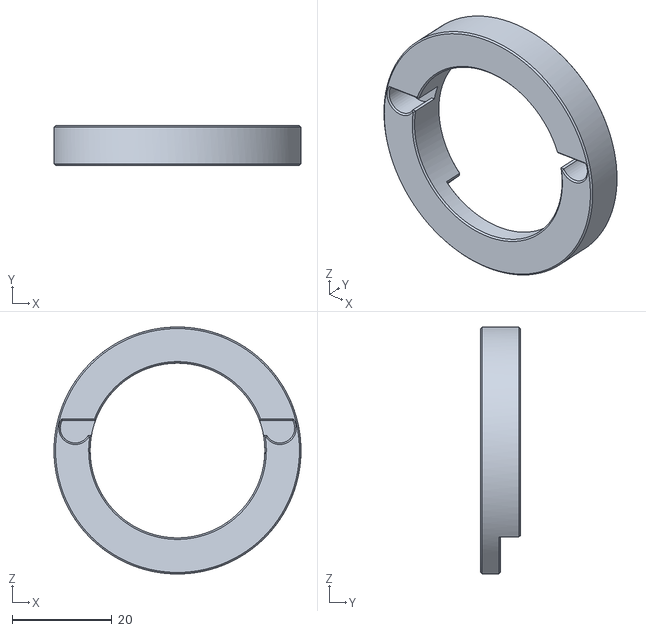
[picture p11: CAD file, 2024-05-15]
hardware/3Dprints/v0-1-0/R3.stl
49.5 x 8.00 x 49.5

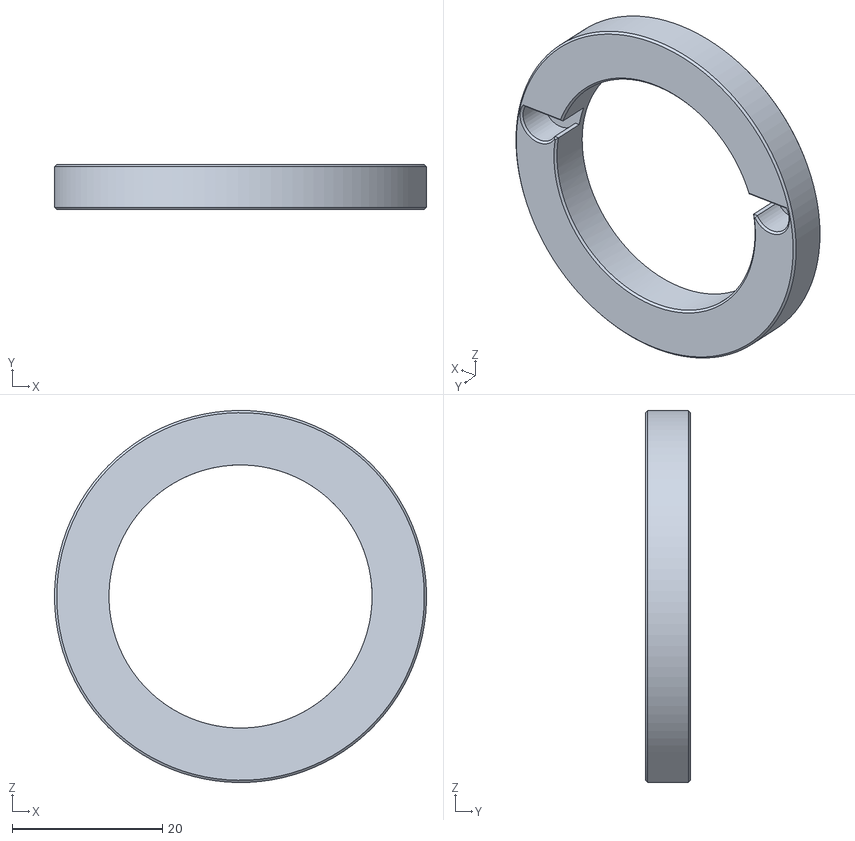
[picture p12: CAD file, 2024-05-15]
hardware/3Dprints/v0-1-0/R4.stl
49.5 x 6.00 x 49.5

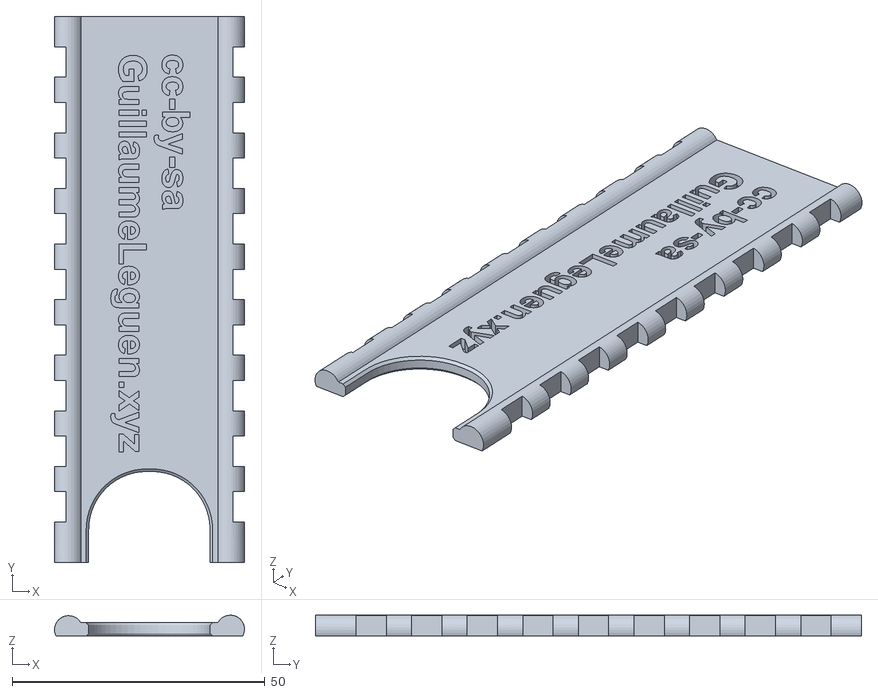
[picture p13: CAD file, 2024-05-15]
hardware/3Dprints/v0-1-0/S1.stl
37.6 x 108.0 x 4.10

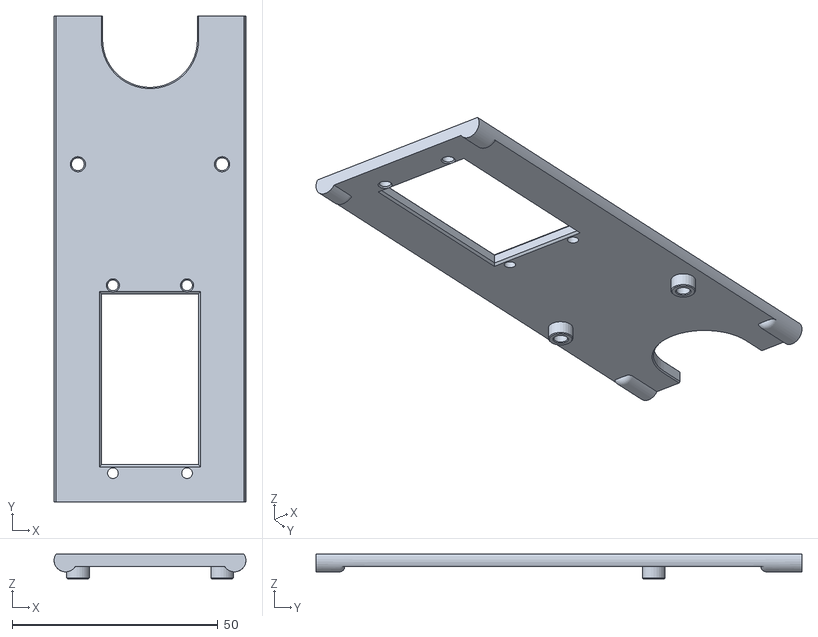
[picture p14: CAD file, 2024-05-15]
hardware/3Dprints/v0-1-0/S2.stl
46.6 x 118.0 x 6.00

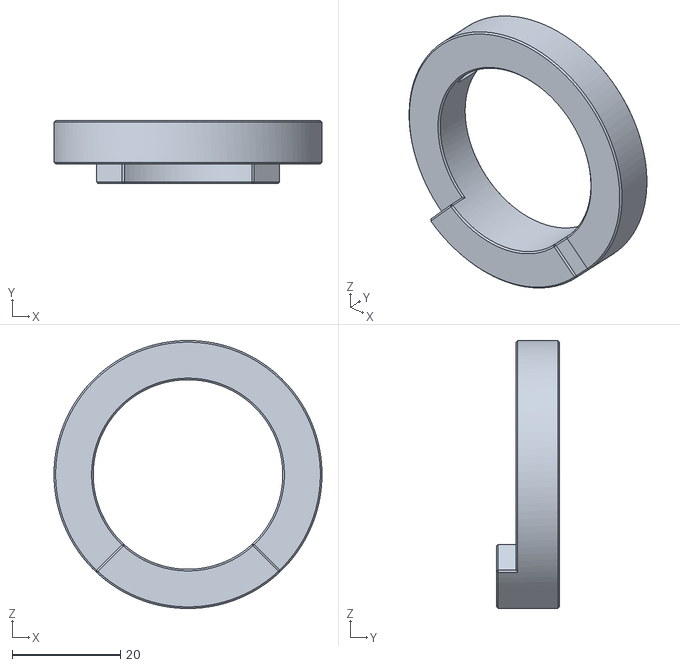
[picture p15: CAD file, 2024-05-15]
hardware/3Dprints/v0-1-0/R2.stl
49.5 x 11.6 x 49.5

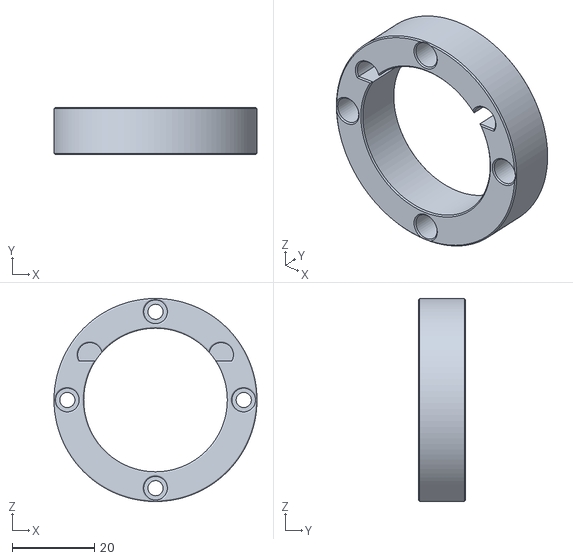
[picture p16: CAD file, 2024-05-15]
hardware/3Dprints/v0-1-0/R1.stl
49.5 x 11.5 x 49.5

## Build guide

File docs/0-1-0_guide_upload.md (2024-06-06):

# D. Guide de programmation (v1.0)
Ce présent guide détail le programme de la sonde de température. En aucun cas il n'abordera comment utiliser le logiciel Arduino IDE pour programmer une carte électronique. Pour apprendre cette manipultaion élémentaire d'arduino, sé référer à des tutoriels en lignes (mots clés : téléverser, arduino, C++).  

## 1/ Prérequis
 * [Avoir installé le logiciel Arduino IDE compatible avec votre système d'exploitation.](https://www.arduino.cc/en/software) 
 * [Avoir installé les pilotes nécéssaires pour la carte adafruit adalogger M0 sur Arduino IDE en suivant le tutoriel proposé par adafruit. ](https://learn.adafruit.com/adafruit-feather-m0-adalogger/setup)
 * Avoir installé les librairies :
   * [Wire](https://www.arduino.cc/reference/en/language/functions/communication/wire/)
   * [RTClib](https://www.arduino.cc/reference/en/libraries/rtclib/)
   * [TSYS01](https://github.com/bluerobotics/BlueRobotics_TSYS01_Library.git) (Librairie pour le capteur de température Blue robotics)
   * [SPI](https://www.arduino.cc/reference/en/language/functions/communication/spi/)
   * [SD](https://www.arduino.cc/reference/en/libraries/sd/)

## 2/ Programme
Le programme (Software) de la sonde de température est disponible dans l'archive au chemin suivant : ```/software/0-1-0_software_temp/0-1-0_software_temp.ino.```

 * [Télécharger le programme au format .ino](https://github.com/gheleguen/open_educational_ocean_recorder/blob/main/software/0-1-0_software_temp/0-1-0_software_temp.ino)

### 2.1 Détail du programme
<section style="border: 2px solid red; padding: 20px; border-radius:20px; color: red;">
Attention ! Le détail du programme ci-dessous ne reprend pas toutes les lignes du code. Pour programmer la sonde, préférez télécharger le fichier présent dans l'archive. </section>

#### 2.1.1 Les variables paramétrables

Dans cette section, il est possible de modifier les variables de temps. La sonde est programmé pour réaliser une série de mesures à intervalles réguliers. Tel que :

            M1 M2 M3 - - -Mn            M1 M2 M3 - - -Mn            M1 M2 M3 - - -Mn

 - L’intervalle entre deux séries de mesures est représenté par la variable **"delay_read_temp"**
 - Le nombre de répétitions pour chacune des séquences de prises de mesures **"repetition_mesures"**
 - L’intervalle entre chacune des répétition est défini par la variable : **"repetition_mesures"**

```c++
int delay_read_temp = 10000 ; // Temps entre chacune des série de prises de mesures
int repetition_mesures = 5 ; // Nombre de Répétitions de prises de mesures
int delay_repetition_temp = 10 ; // Temps entre chacune des répétitions
```

Ici on appel les librairies nécessaires pour l'éxecution du programme : 

```c++
//Fonctions d'appel de librairies (I2C et Wire) pour l'horloge RTC DS3231
#include <Wire.h>
#include "RTClib.h"

//Librairie pour lire le capteur de température
#include "TSYS01.h"

//Périphérique de série et la Librairie de la carte SD
#include <SPI.h> //serial peripheral interface for SD card reader
#include <SD.h> //library for SD card reader
```

Quelques variables de branchements qu'il pourrait-être nécessaire de modifier si vous n'utilisez pas tout à fait le même matériel.
```c++
// Définition des variables
float temp;
const int chipSelect = 4; //Broche de lecture du RTC
char datalogFileName[25];
char dateTimeString[40];
int Date2;
int x ;  delay(5000);
pinMode(led, OUTPUT);
int led = 6; // Broche du voyant lumineux
```

#### 2.1.2 Initialisation

Le moniteur série devra être réglé sur 9600 pour permettre la lecture lorsque la carte Arduino sera connecté au PC en USB. 
```c++
  Serial.begin(9600);
```

Initialisation de la carte SD. Dans le cas où la carte serait introuvable, aucun fichier ne sera créé et aucune mesure ne sera prise. 
```c++
  //Initialisation de la carte SD
  Serial.println("Initialisation de la carte SD...");

  if (!SD.begin(chipSelect)) {
    Serial.println("Erreur de lecture de carte SD, ou carte non présente.");
    while (1);
  }
  Serial.println("Carte SD initialisé.");

  /* Cette fonction permet à la bibliothèque SD de définir les dates correctes de création et de modification des fichiers pour tous les fichiers de la carte SD.
  SdFile::dateTimeCallback(SDCardDateTimeCallback);*/
  digitalWrite(led, HIGH);   // LED allumé
  delay(1000);
```

Ici, on teste l'horloge RTC. Puis on l'initialise. Dans le cas où la RTC aurai perdu l'heure, et sera automatiquement réglé sur l'heure de l'ordinateur qui l'a programmé. 
```c++
  //Essai de la lecture du RTC. Si l'horloge est introuvable le programme ne pourra se dérouler. 
  if (! rtc.begin()) {
    Serial.println("Erreur, RTC introuvable.");
    while (1);
  }
  
  //Initialisation de l'horloge RTC sur l'heure de l'ordinateur au téléversement.
  if (rtc.lostPower()) {

    //reset RTC with time when code was compiled if RTC loses power
    Serial.println("RTC lost power, lets set the time!");
    rtc.adjust(DateTime(F(__DATE__), F(__TIME__)));
  }
  get_numbered_filename(datalogFileName,"LOG" , "CSV");
```

Initialisation de fichier de stockage de données sur la carte SD. Certaines fonctions appel à des sous-fonctions qui seront détaillés plus bas. 
```c++
  // Initialisation du fichier de données LOG en .csv
  Serial.print("Ecriture dans le datalog: ");
  Serial.println(datalogFileName);

  File dataFile = SD.open(datalogFileName, FILE_WRITE);
  delay(250); 

  if (dataFile) {
    Serial.println("====================================================");
    Serial.println("Date,Time [UTC],Temp [°C]");
    dataFile.println("Date,Time [UTC],Temp [°C]");
    dataFile.close();

  }
  // Si le datalog ne peut-être ouvert, un message d'erreur s'affichera sur le moniteur série.
  else {
    Serial.println("Erreur: Impossible d'ouvrir le datalog");
  }

  Serial.println("Starting mesurements");
  Wire.begin();

  sensor.init();
  digitalWrite(led, LOW);   // LEd etteinte
}
```

#### 2.1.3 Boucle

Au début de la boucle on initialise la variable "x" à 0. Cette variable permet de compter le nombre de mesures de reproductions pour chacune des phases.
```c++
  x=0;
```

Tant que le nombre de répétitions de mesures n'est pas atteinte, le programme reproduit une mesure.
```c++
  while (x < repetition_mesures){
    digitalWrite(led, HIGH);   // LEd allumé
    DateTime now = rtc.now(); //check RTC
    get_date_time_string(dateTimeString, now);
    temp = sensor.temperature();

    // Lecture de la température
    sensor.read();

    // Ecriture des données sur le moniteur série
    Serial.print(dateTimeString);
    Serial.print(",");
    Serial.println(temp);
  
    //Stockage de la donnée dans le fichier de données
    File dataFile = SD.open(datalogFileName, FILE_WRITE);
    if (dataFile) {
      dataFile.print(dateTimeString);
      dataFile.print(",");
      dataFile.println(temp);
      dataFile.close();
      x = x+1;
      delay(delay_repetition_temp); // Attente entre chacune des mesures de répétition
    }
  }
```

La LED s'allume à chacune des prise de mesure de température. 
```c++
  digitalWrite(led, LOW);   // LEd etteinte
```

Cette fonction permet d'attendre le temps nécessaire avant de reproduire une séquence de mesure.
```c++
  delay(delay_read_temp); // Attente avant nouvelle séquence de mesures
```

#### 2.1.4 Fonctions secondaires

Fonction permettant le nommage du fichier de données. Elle utilise les données de date et d'heure. 
```c++
void get_numbered_filename(char* outStr, char* filePrefix, char* fileExtension) {

  //sprintf(outStr, "%s000.%s", filePrefix, fileExtension);
  DateTime now = rtc.now();
  Date2 = now.year()-2000;
  sprintf(outStr,"%02d%02d%02d00.%s",Date2,now.month(),now.day(),fileExtension); 
  int namelength = strlen(outStr);
  if (namelength > 12) Serial.println("Erreur: Nom de fichier trop long. Réduire votre nom de fichier à moins de 5 caractères (12 caractères maximum en incluant l'extension) !");

  int i = 1;
  while (SD.exists(outStr)) { 

    int hundreds = i / 100;
    outStr[namelength - 6] = '0' + (i / 10) - (hundreds * 10);
    outStr[namelength - 5] = '0' + i % 10;
    i++;
  }
}
```

Fonction d'écriture de l'heure et de la date sur chaque ligne du tableau.
```c++

void get_date_time_string(char* outStr, DateTime date) {
  sprintf(outStr, "%02d/%02d/%02d,%02d:%02d:%02d", date.year(), date.month(), date.day(), date.hour(), date.minute(), date.second());
  // Note: If you would like the date & time to be seperate columns change the space in the formatting string to a comma - this works because the file type is CSV (Comma Seperated Values)
}
```

### 2.2 Programme complet

En date du : 06/06/2024

```c++
/*
 * Ce programme écrit en C++ est destiné à une sonde de température de fond réalisé par Guillaume Leguen (guillaumeleguen.xyz).
 * Retrouvez la totalité du projet sur readthe doc : https://open-educational-ocean-recorder.readthedocs.io/fr/latest/
 * 
 * Licence : open_educational_ocean_recorder est un projet de Guillaume Leguen proposé sous licence CC-by-sa 4.0
 * Ce programme est basé en partie sur le travail d'oceanography for everyone (https://oceanographyforeveryone.com/)
*/

// Les paramétres suivant peuvent être modifiés comme réglage de la sonde
int delay_read_temp = 10000 ; // Temps entre chacune des série de prises de mesures
int repetition_mesures = 5 ; // Nombre de Répétitions de prises de mesures
int delay_repetition_temp = 10 ; // Temps entre chacune des répétitions

//Fonction d'appel de librairies (I2C et Wire) pour l'horloge RTC DS3231
#include <Wire.h>
#include "RTClib.h"

//Librairie pour lire le capteur de température
#include "TSYS01.h"

//Périphérique de série et la Librairie de la carte SD
#include <SPI.h> //serial peripheral interface for SD card reader
#include <SD.h> //library for SD card reader

TSYS01 sensor;
RTC_DS3231 rtc; // Commenter si utilisation de l'autre RTC
//RTC_PCF8523 rtc; //Décommenter si utilisation de ce RTC

// Définition des variables
float temp;
const int chipSelect = 4; //Broche de lecture du RTC
char datalogFileName[25];
char dateTimeString[40];
int Date2;
int x ;
int led = 6; // Brche du voyant lumineux

// Actions d'initialisation
void setup() {

  Serial.begin(9600);
  delay(5000);
  pinMode(led, OUTPUT);
  //Initialisation de la carte SD
  Serial.println("Initialisation de la carte SD...");

  if (!SD.begin(chipSelect)) {
    Serial.println("Erreur de lecture de carte SD, ou carte non présente.");
    while (1);
  }
  Serial.println("Carte SD initialisé.");

  /* Cette fonction permet à la bibliothèque SD de définir les dates correctes de création et de modification des fichiers pour tous les fichiers de la carte SD.
  SdFile::dateTimeCallback(SDCardDateTimeCallback);*/
  digitalWrite(led, HIGH);   // LED allumé
  delay(1000);

  //Essai de la lecture du RTC. Si l'horloge est introuvable le programme ne pourra se dérouler. 
  if (! rtc.begin()) {
    Serial.println("Erreur, RTC introuvable.");
    while (1);
  }
  
  //Initialisation de l'horloge RTC sur l'heure de l'ordinateur au téléversement.
  if (rtc.lostPower()) {

    //reset RTC with time when code was compiled if RTC loses power
    Serial.println("RTC lost power, lets set the time!");
    rtc.adjust(DateTime(F(__DATE__), F(__TIME__)));
  }
  get_numbered_filename(datalogFileName,"LOG" , "CSV");

  // Initialisation du fichier de données LOG en .csv
  Serial.print("Ecriture dans le datalog: ");
  Serial.println(datalogFileName);

  File dataFile = SD.open(datalogFileName, FILE_WRITE);
  delay(250); 

  if (dataFile) {
    Serial.println("====================================================");
    Serial.println("Date,Time [UTC],Temp [°C]");
    dataFile.println("Date,Time [UTC],Temp [°C]");
    dataFile.close();

  }
  // Si le datalog ne peut-être ouvert, un message d'erreur s'affichera sur le moniteur série.
  else {
    Serial.println("Erreur: Impossible d'ouvrir le datalog");
  }

  Serial.println("Starting mesurements");
  Wire.begin();

  sensor.init();
  digitalWrite(led, LOW);   // LEd etteinte
}

// Début du programme en boucle
void loop() {
  x=0;

  // Tant que le nombre de répétition de mesure n'est pas atteinte, le programme reproduit une mesure
  while (x < repetition_mesures){
    digitalWrite(led, HIGH);   // LEd allumé
    DateTime now = rtc.now(); //check RTC
    get_date_time_string(dateTimeString, now);
    temp = sensor.temperature();

    // Lecture de la température
    sensor.read();

    // Ecriture des données sur le moniteur série
    Serial.print(dateTimeString);
    Serial.print(",");
    Serial.println(temp);
  
    //Stockage de la donnée dans le fichier de données
    File dataFile = SD.open(datalogFileName, FILE_WRITE);
    if (dataFile) {
      dataFile.print(dateTimeString);
      dataFile.print(",");
      dataFile.println(temp);
      dataFile.close();
      x = x+1;
      delay(delay_repetition_temp); // Attente entre chacune des mesures de répétition
    }
  }
  digitalWrite(led, LOW);   // LEd etteinte
  delay(delay_read_temp); // Attente avant nouvelle séquence de mesures

}

// Fonction de nommage du fichier de données.
void get_numbered_filename(char* outStr, char* filePrefix, char* fileExtension) {

  //sprintf(outStr, "%s000.%s", filePrefix, fileExtension);
  DateTime now = rtc.now();
  Date2 = now.year()-2000;
  sprintf(outStr,"%02d%02d%02d00.%s",Date2,now.month(),now.day(),fileExtension); 
  int namelength = strlen(outStr);
  if (namelength > 12) Serial.println("Erreur: Nom de fichier trop long. Réduire votre nom de fichier à moins de 5 caractères (12 caractères maximum en incluant l'extension) !");

  int i = 1;
  while (SD.exists(outStr)) { 

    int hundreds = i / 100;
    outStr[namelength - 6] = '0' + (i / 10) - (hundreds * 10);
    outStr[namelength - 5] = '0' + i % 10;
    i++;

  }

}

// Fonction d'écriture de l'heure et de la date.
void get_date_time_string(char* outStr, DateTime date) {
  sprintf(outStr, "%02d/%02d/%02d,%02d:%02d:%02d", date.year(), date.month(), date.day(), date.hour(), date.minute(), date.second());
  // Note: If you would like the date & time to be seperate columns change the space in the formatting string to a comma - this works because the file type is CSV (Comma Seperated Values)
}

// Fonction permettant à la bibliothèque SD de définir les dates correctes de création et de modification des fichiers pour tous les fichiers de la carte SD 
void SDCardDateTimeCallback(uint16_t* date, uint16_t* time)
{
  DateTime now = rtc.now();
  *date = FAT_DATE(now.year(), now.month(), now.day());
  *time = FAT_TIME(now.hour(), now.minute(), now.second());
}
```

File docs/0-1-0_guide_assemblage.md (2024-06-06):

# C. Guide d'assemblage (v1.0)
Ce présent guide d'assemblage, suppose que vous ayez réalisés les étapes précédentes et nottamment l'étape du sourcing. Vérifiez avoir reçu tous les composants avant de commencer. 
Avant de réaliser le montage de la sonde, il peut-être utile de vérifier le bon fonctionnement des capteurs. Pour cela suivez les protocoles de tests disponibles en Annexes de ce chapitre. 
 - [Tester le capteur de temprérature](0-0-1_test_temp-sensor.md)
 - [Tester l'horloge RTC](0-0-1_test_set_rtc-ds3231.md)

## 1/ Préparations, câblages et soudures
### 1.1 Connectique du capteur de température

 - Rassembler le capteur de température (et ses accessoires, le joint et l'écrou), un bloc connectique mâle JST 4 voies (4P Plug Housing), 4 ferrures mâles JST à sertir, ainsi qu'une bride à 2 perforations (ou une plaque alu deux perforations). 
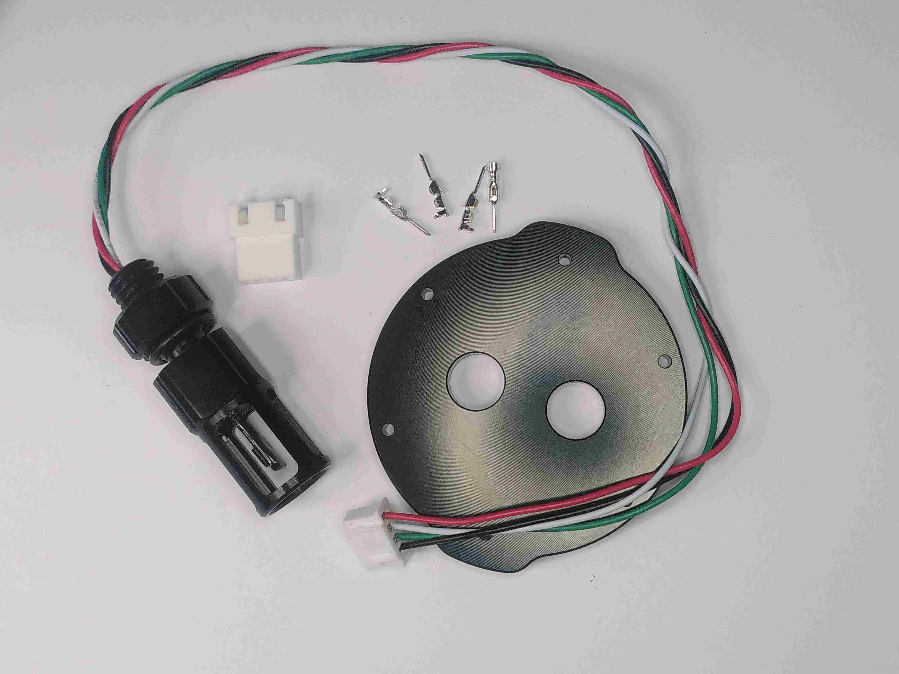
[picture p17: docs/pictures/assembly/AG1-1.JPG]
Photo montrant les éléments nécessaires

 - A l'aide d'une pince coupante, sectionner le connecteur du capteur déjà en place. Veiller à couper au plus proche du connecteur afin de conserver un maximum de fil.
 - Dénuder chacun des fils au moyen d'une pince à dénuder. 
 - Sertir au bout de chaque fil une ferrure mâle.

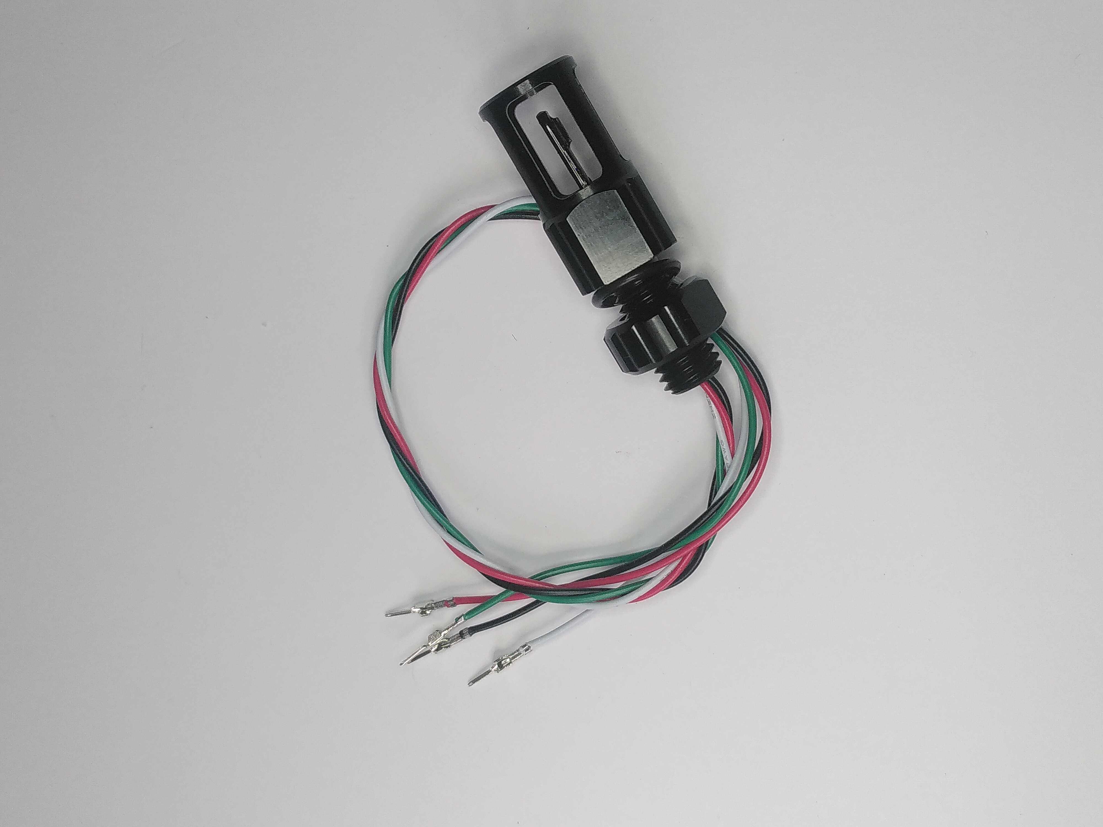
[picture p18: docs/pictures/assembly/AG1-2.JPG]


<section style="border: 2px solid red; padding: 20px; border-radius:20px; color: red;">
Attention ! Avant de positionner les ferrures dans le bloc connecteur JST, il faudra passer le capteur dans un trou de la bride. Ceci ne pouvant pas être fait après car le connecteur ne passe pas dans la perforation de la bride. </section>

 - Positionner le joint torique du coté extérieur, puis passer le pénétrateur dans la bride, pour enfin serrer avec l'écrou à la main puis à l'aide d'une clé. 

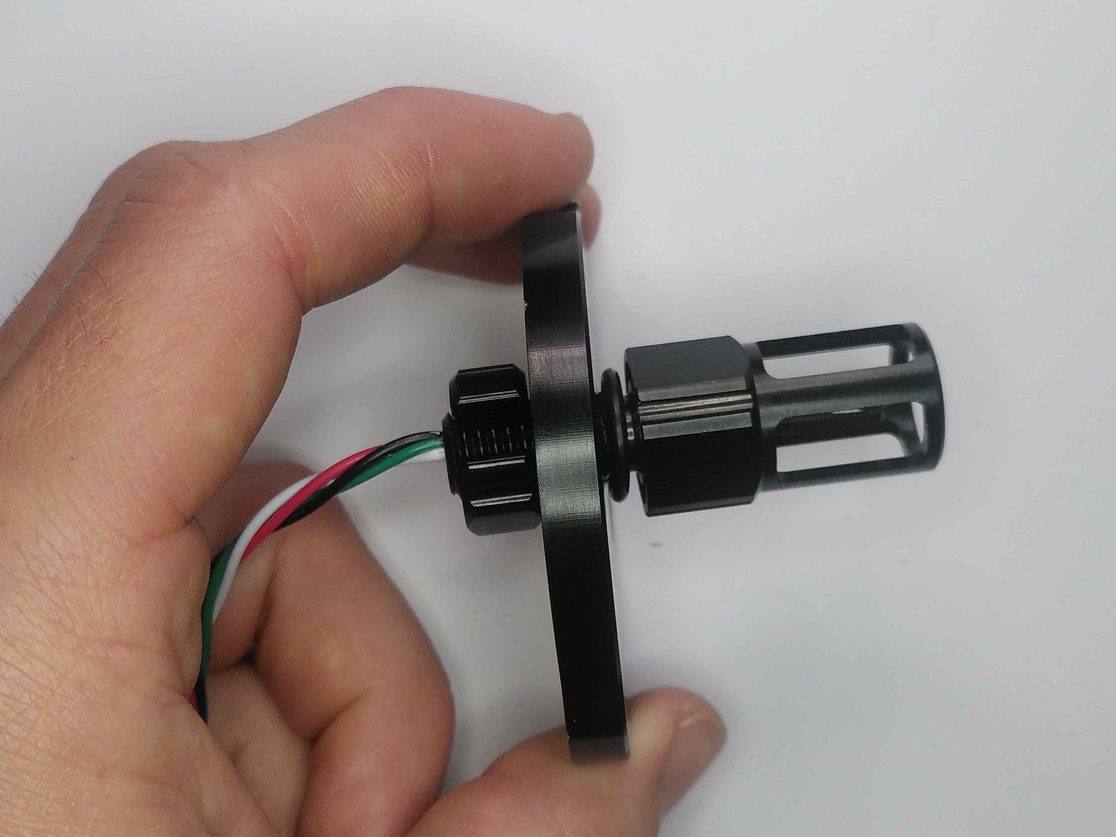
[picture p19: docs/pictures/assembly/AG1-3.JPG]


 - Enfoncer chacun des fil dans le connecteur JST. En suivant le schéma ci-dessous. 

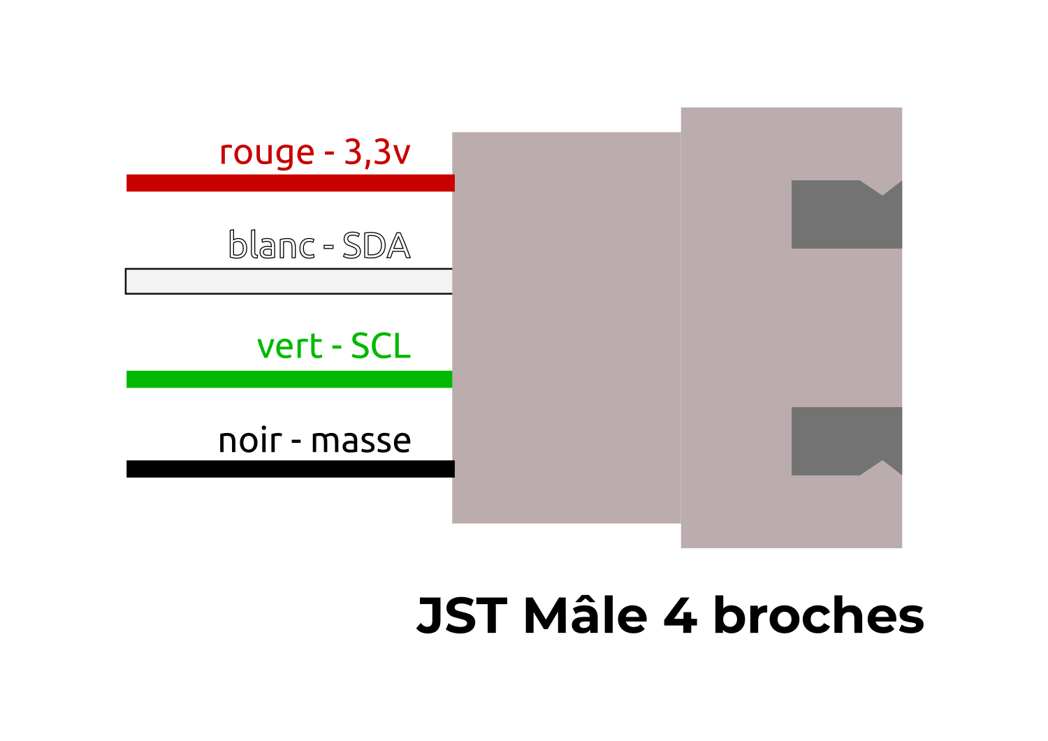
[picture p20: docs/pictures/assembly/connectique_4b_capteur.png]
Schèma d'implantation des fils du capteur.

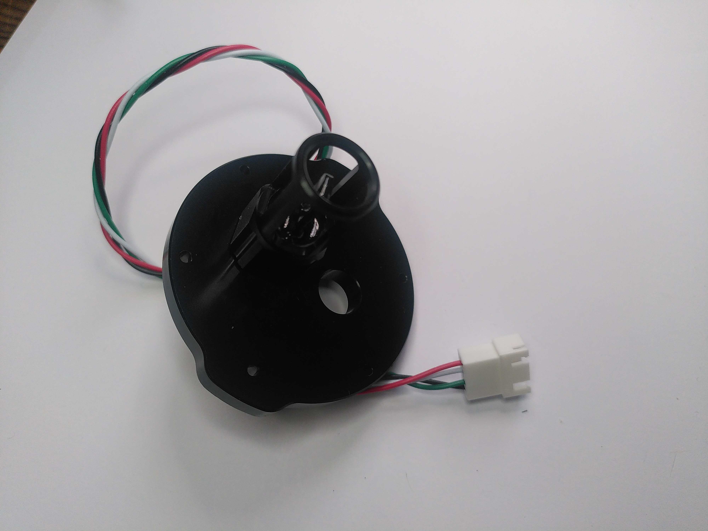
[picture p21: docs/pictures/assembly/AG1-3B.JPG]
Photo montrant le capteur de température et le connecteur JST en place


### 1.2 Préparation du micro-controleur 

 - Rassembler l'horloge (la carte RTC), et 2 lignes de broches dupont mâle (1* 16 broches et 1* 12 broches).

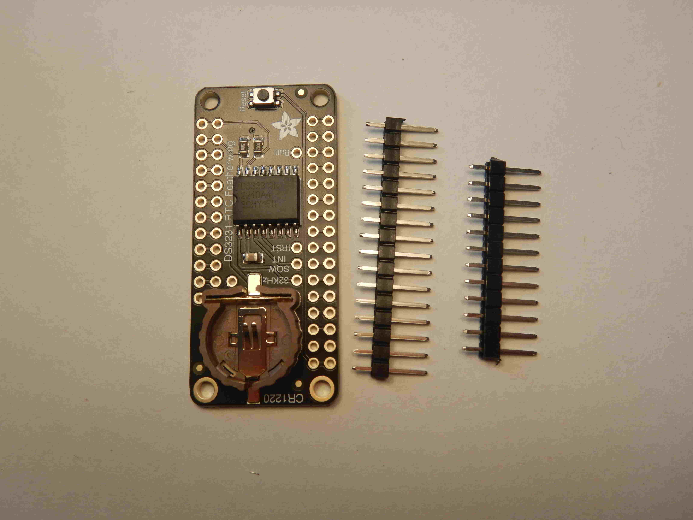
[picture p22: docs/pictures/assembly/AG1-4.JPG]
Photo montrant l'horloge RTC au coté des deux connecteurs duponts mâle.


 - Souder ces deux connecteurs duponts comme suit. 

<section style="border: 2px solid red; padding: 20px; border-radius:20px; color: red;"><b>Attention</b> à veiller à :
<li>Souder les broches sur les emplacements externes</li>
<li>Positionner les broches à l'opposé de l'emplacement de la pile. </li>
<li>Souder les broches les plus courtes.</li>
<li>Veiller à maintenir les broches bien perpendiculaire à la plaque. </li>
</section>

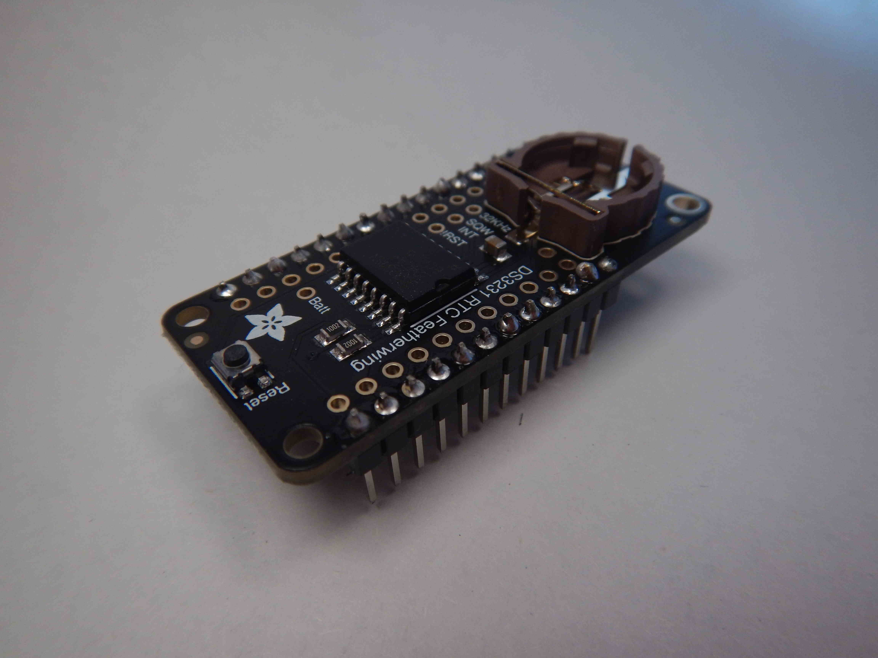
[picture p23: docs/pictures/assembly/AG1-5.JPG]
On a soudé les deux broches duponts sur la carte d'horloge RTC


 - Rassembler l'horloge RTC qui viens d'être soudé ainsi que deux nouvelles lignes de broches (1* 16 broches et 1* 11 broches).

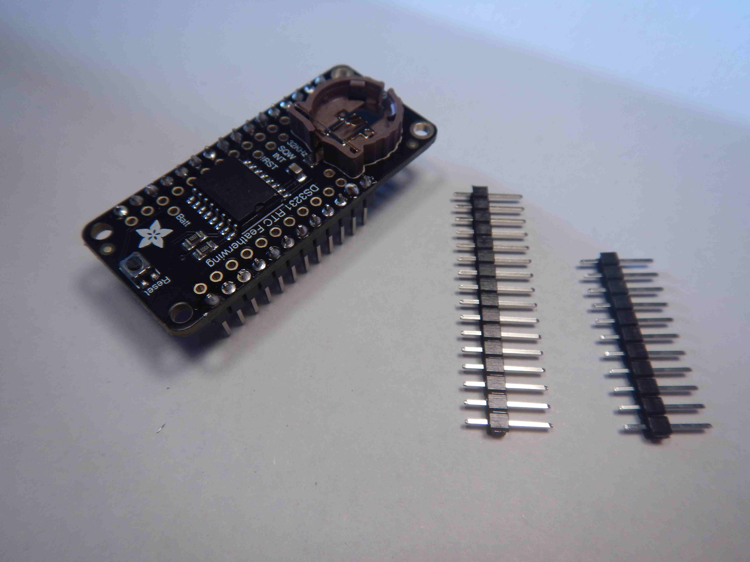
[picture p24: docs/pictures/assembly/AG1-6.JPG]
La carte RTC et des broches


 - Souder ces broches à l'opposé des broches installé à l'étape précédente. 

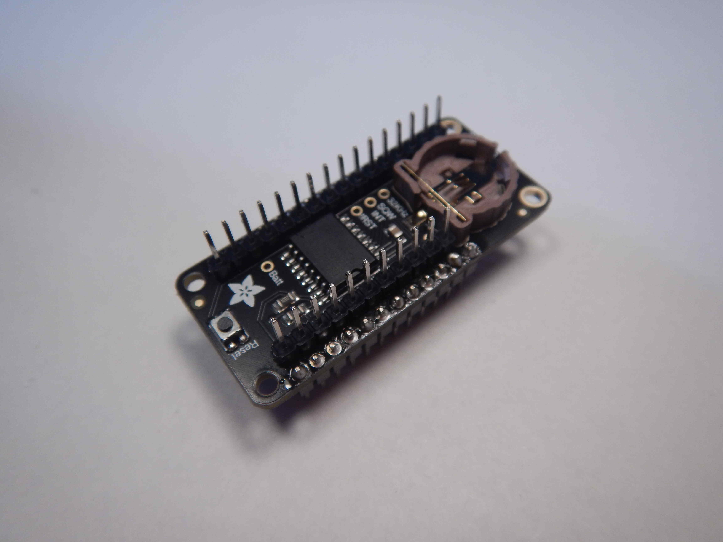
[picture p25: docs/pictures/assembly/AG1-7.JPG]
On a soudé les deux nouvelles broches duponts sur la carte d'horloge RTC


 - Rassembler le microcontrôleur (Adafruit MO), ainsi que deux lignes de broches dupont femelles (1* 16 broches et 1* 12 broches).
 
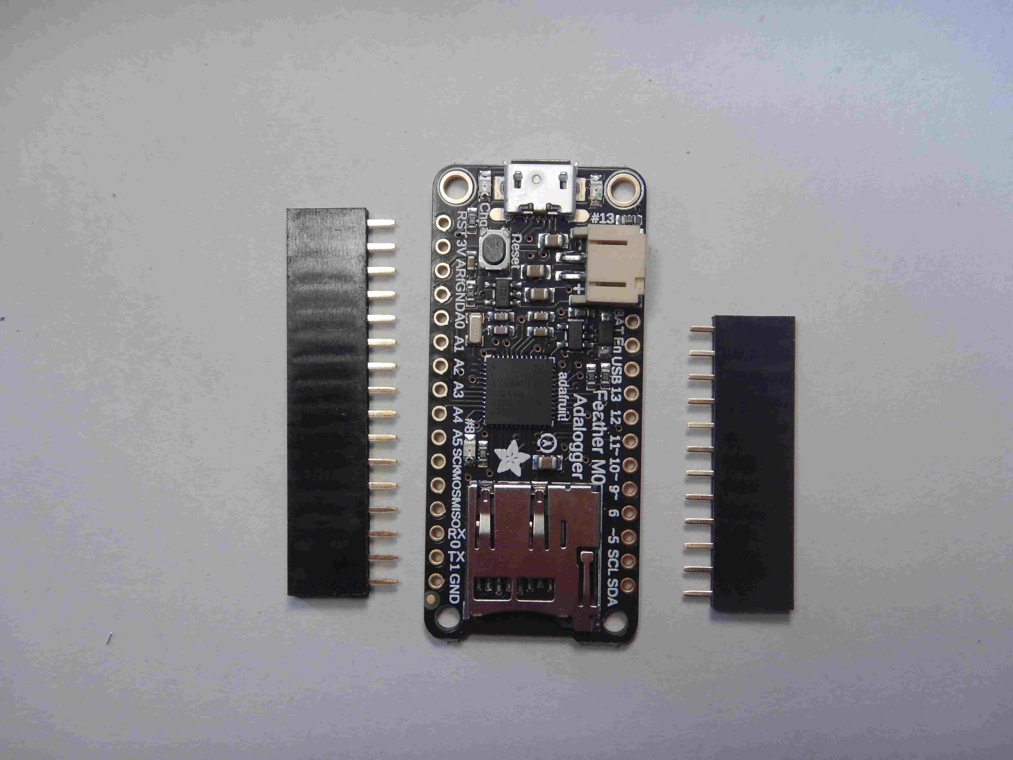
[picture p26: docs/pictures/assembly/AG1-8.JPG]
La carte Adafruit M0 et des broches femelles


 - Souder ces broches en veillant au sens. Le coté femelle doit se retrouver au dessus de la carte.
 - C'est ici que viendra se brancher l'horloge RTC. 

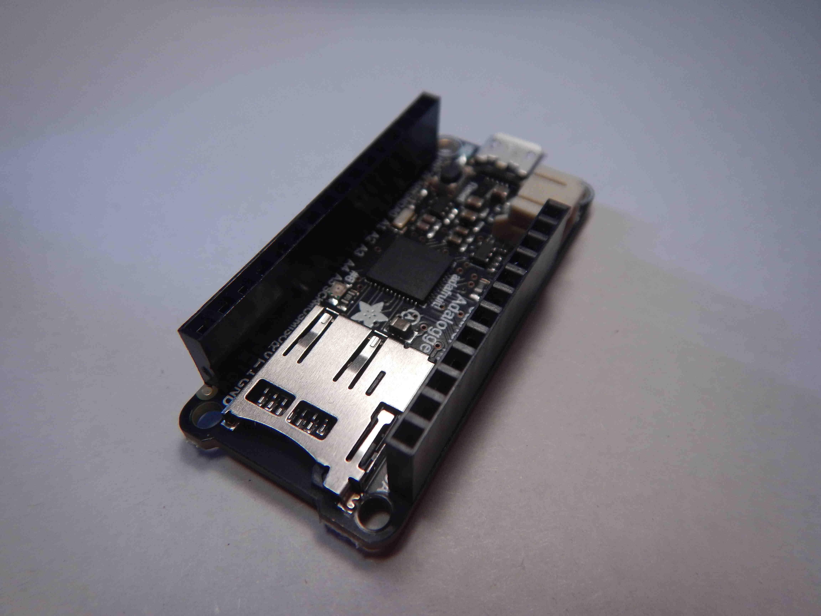
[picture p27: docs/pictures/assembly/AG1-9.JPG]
On a soudé les deux broches duponts femelles sur la carte Adafruit M0


 - Enfin, assembler les deux cartes électronique l'une sur l'autre. 
 - L'horloge RTC viendra donc au dessu du micro-contrôleur. 

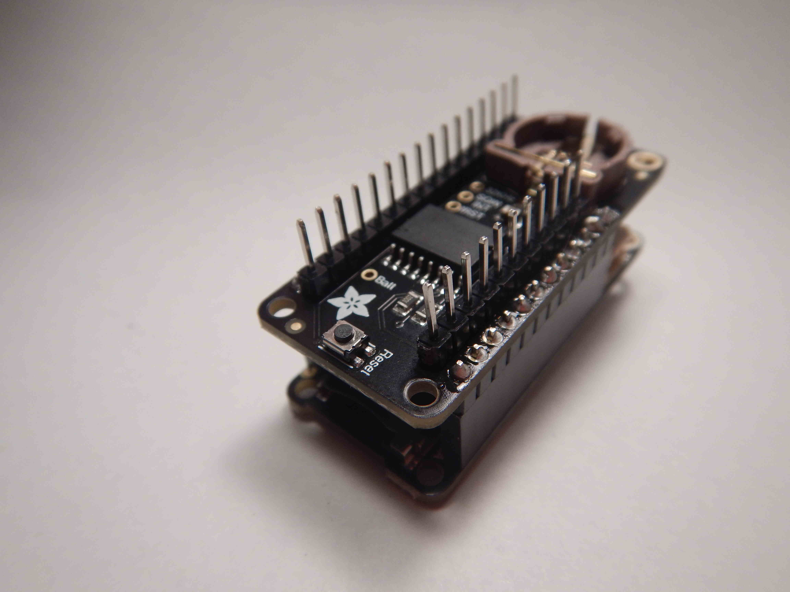
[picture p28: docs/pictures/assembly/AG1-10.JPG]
Assemblage des deux cartes électroniques


### 1.3 Assemblage du circuit secondaire
Le circuit secondaire, va permettre dans un premier temps de faciliter les connexions entre capteurs et voyants. Il permet aussi d'ajouter des composants nécéssaires comme les résistances de tirages sur le capteur qui communique suivant le protocole I2C.

 - Rassembler, une plaque de prototypage adafruit, trois connecteurs JST mâles à souder 5, 4 et 2 broches, 2 résistances de 10 kohm, du fil électrique à souder.

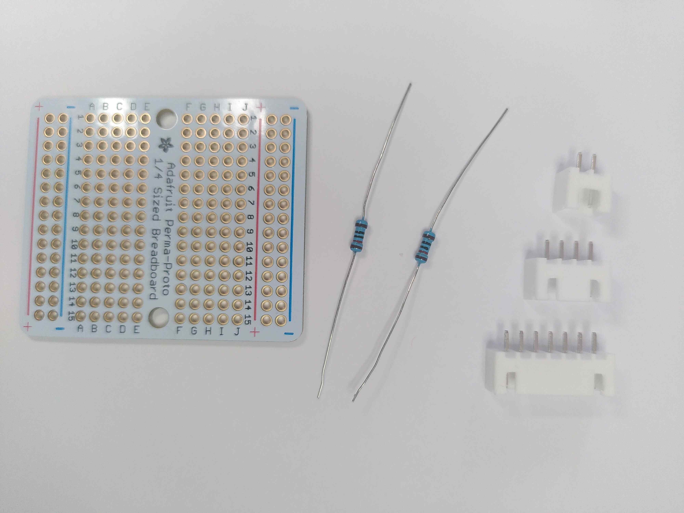
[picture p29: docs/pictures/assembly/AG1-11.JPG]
Fournitures pour soudure sur carte secondaire
 

 - Prendre la plaque de prototypage dans le sens où les lettres des colonnes demeurent dans le bon sens pour la lecture.
 - Souder les 3 connecteurs JST femelles en suivant le plan ci-dessous. Le connecteur 5 broches de G1 à G5, le connecteur de 2 broches de G8 à G9 et le connecteur à 4 broches entre G12 et G15.

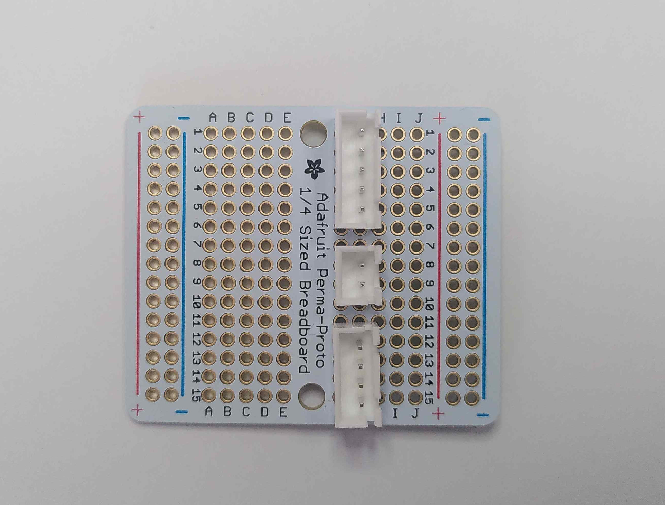
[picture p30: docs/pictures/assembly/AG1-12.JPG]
Implantation des 3 connecteurs m^les sur la carte secondaire


 - Au moyen de trois morceaux de fil (de préférence noir) relier chaque ligne (1, 8 et 12) à la colonne de masse symbolisé par un "-".

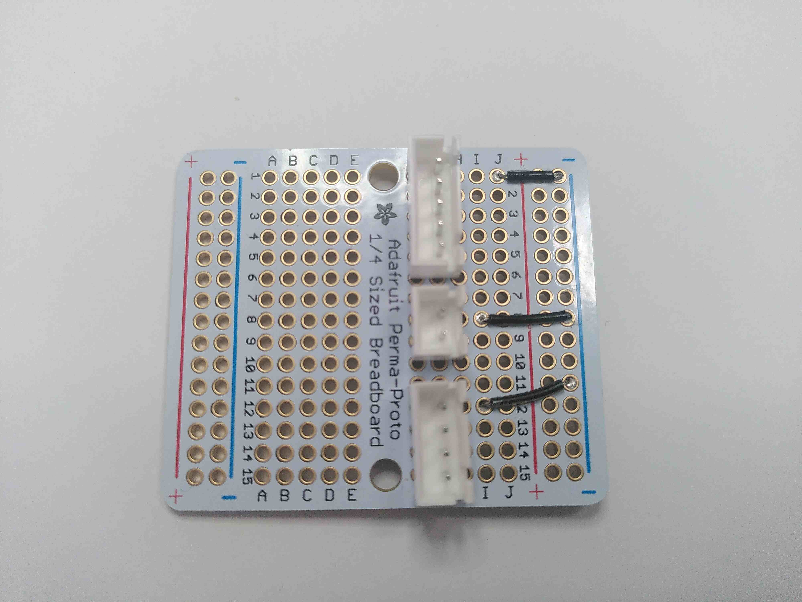
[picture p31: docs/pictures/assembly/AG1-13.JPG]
Implantation des ponts de masses


 - Souder un pont (fil de couleur rouge) entre la ligne 2 et la colonne "+".

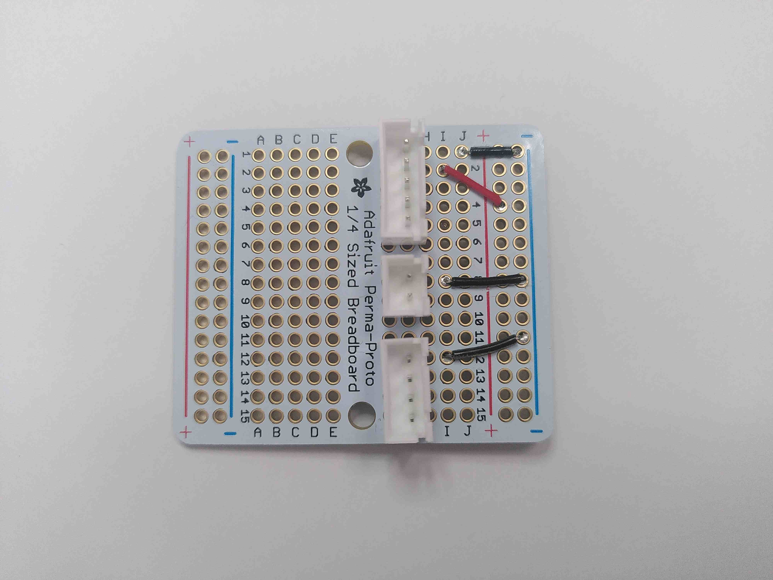
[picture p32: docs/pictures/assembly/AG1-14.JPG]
Implantation fil de +
 

 - Souder un pont (fil bleu) entre les ligens 3 et 9. Il s'agit du fil de donnée logique pour contrôler le voyant lumineux. 

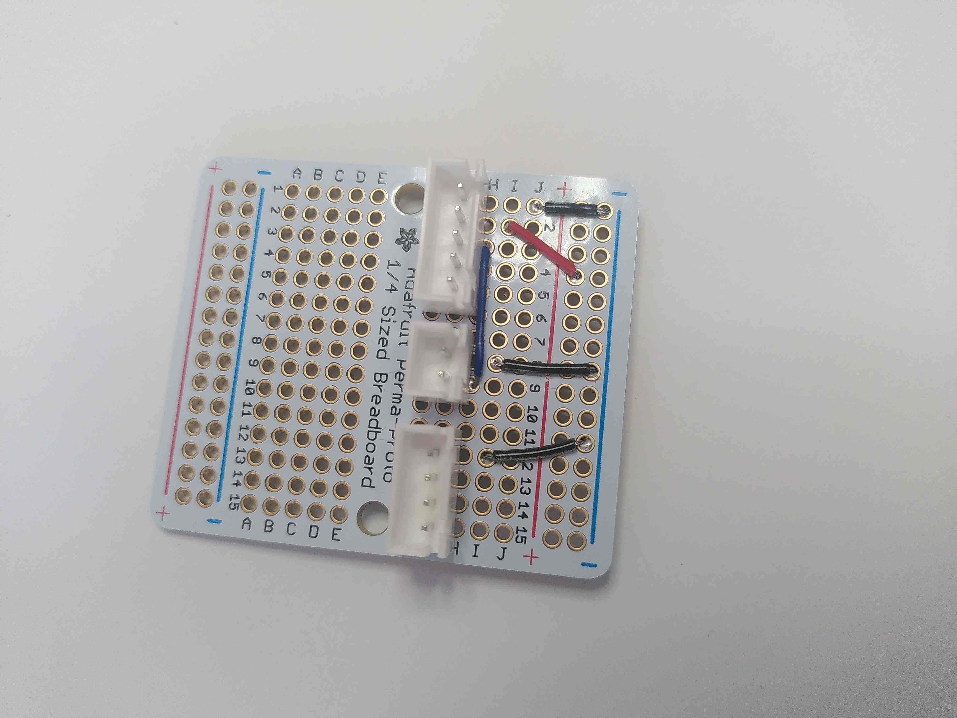
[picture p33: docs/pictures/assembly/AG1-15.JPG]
Implantation fil de data bleu


 - Souder un pont (fil vert) entre les lignes 4 et 13. Il s'agit du SCL, l'horloge pour la lecture du capteur de température. 
 - Souder un pont (fil blanc) entre les lignes 5 et 14. Il s'agit du SDA, le fil de datas pour la lecture du capteur de température. 

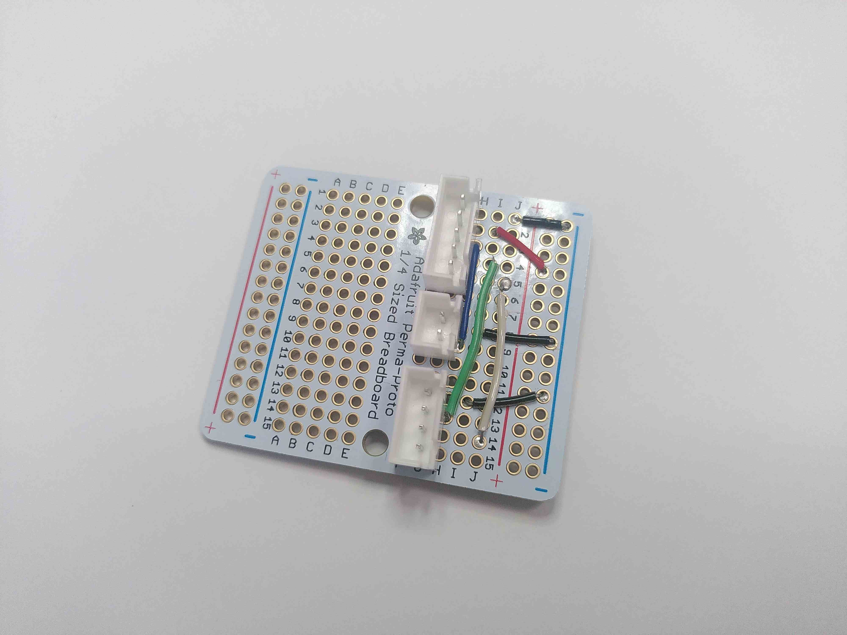
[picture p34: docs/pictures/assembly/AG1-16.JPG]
Implantation fil vert SCL et blanc SDA


 - Souder les deux résistances de 10kohm entre la ligne 13 et le "+" et la seconde entre la ligne 14 et le "+".
 - Se servir d'une des patte de résistance coupé pour faire un pont entre la ligne 15 et la colonne "+".

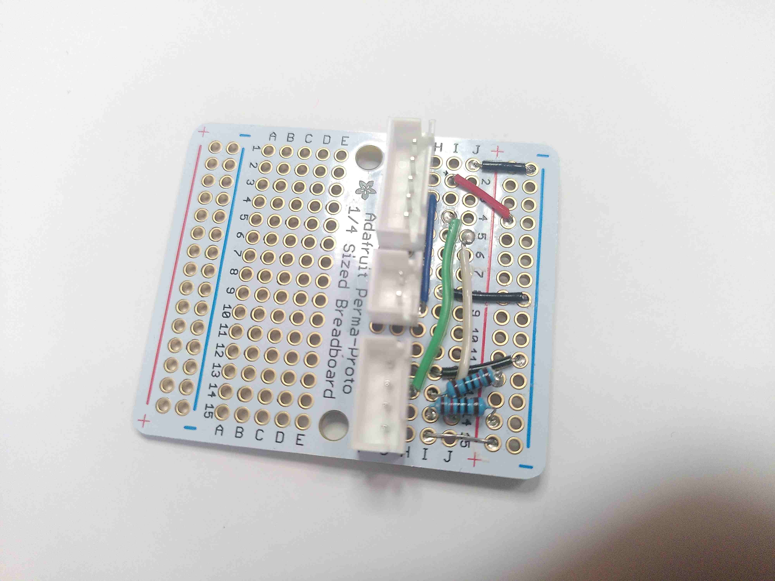
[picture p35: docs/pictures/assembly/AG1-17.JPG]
Implantation des résistances et de l'alimentation du capteur de température
 
 
### 1.4 Connectiques de la batterie
 - Couper un fil du connecteur de la batterie, le dénuder et le souder à un autre fil de même couleur pour le rallonger de 25cm environ. 
 - Isoler la soudure au moyen de gaine thermorétractable. 
 - Faire de même pour rallonger le second fil. 

<section style="border: 2px solid red; padding: 20px; border-radius:20px; color: red;">Attention pendant cette manipulation à ce qu'aucun fil ne se touche pour éviter un court-circuit.</section>

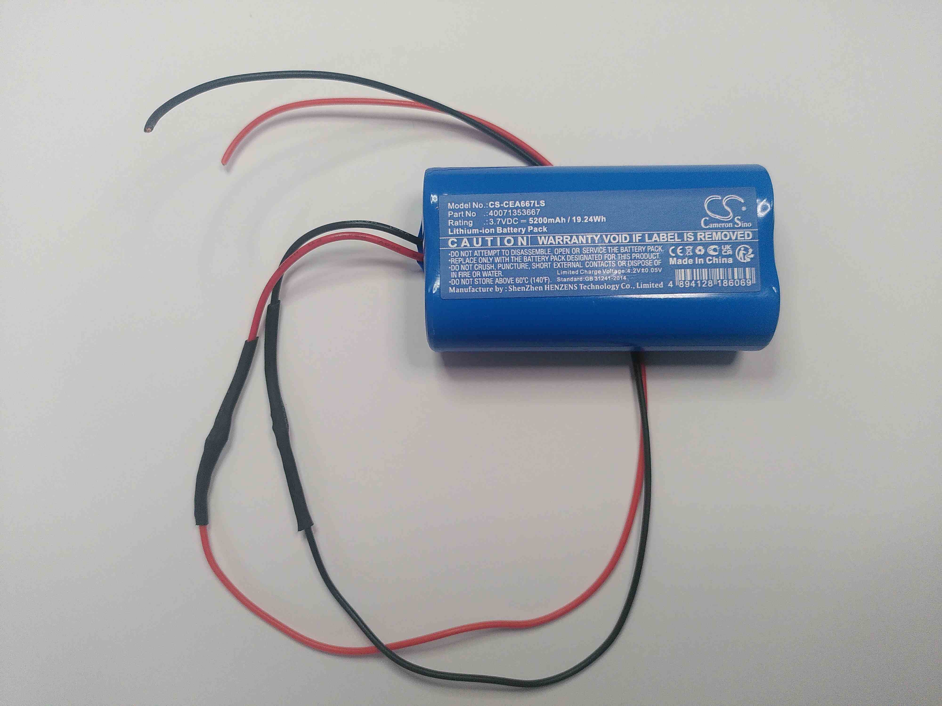
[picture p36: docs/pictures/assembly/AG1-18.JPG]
Rallonge des fils de la batterie


 - Rassembler, la batterie, un connecteur femelle JST à 3 broches (je n'avais pas de 2 broches dans ma boite) et 2 ferrures JST femelles.
 - Dénuder un fil de la batterie, et y sertir une ferrure femelle. 
 - Insérer cette ferrure dans le bloc 3 broches JST mâle. Veiller à respecter le même sens que sur la photo.
 - Faire de même avec le second fil et l'insérer dans le bloc JST à l'opposé du premier.

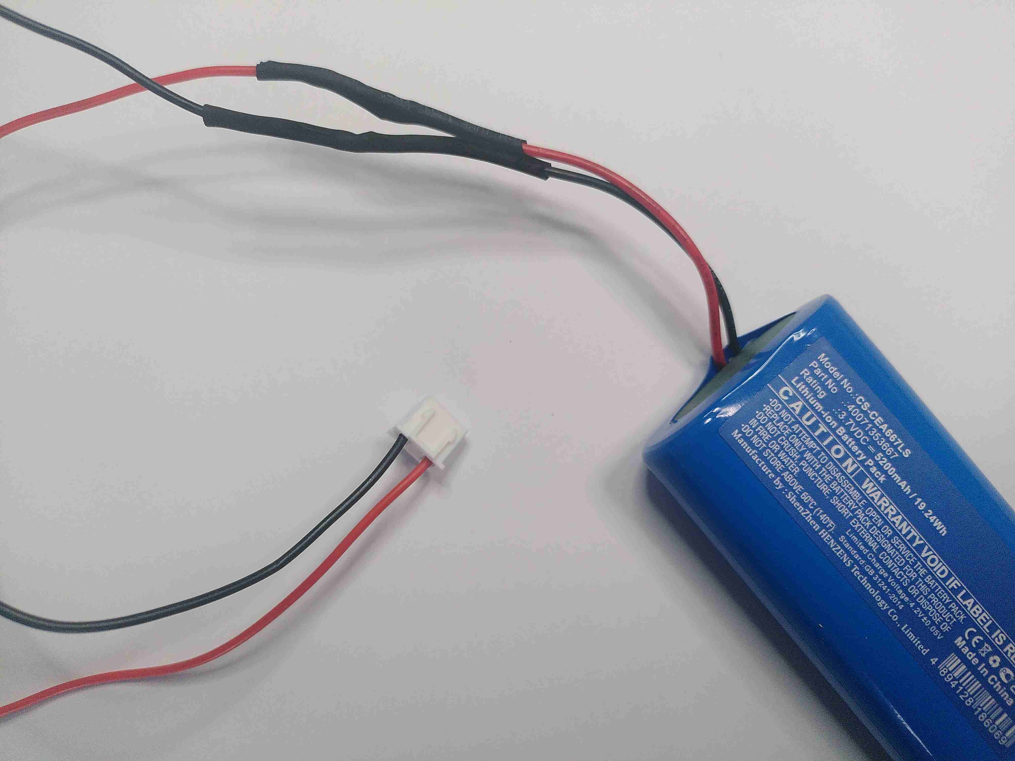
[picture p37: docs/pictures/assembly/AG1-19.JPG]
Implantation du connecteur JST batterie


 - Rassembler, les fils du bouton (switch) étanche, un connecteur JST de batterie, un connecteur JST mâle 3 broches et 2 ferrures mâle.

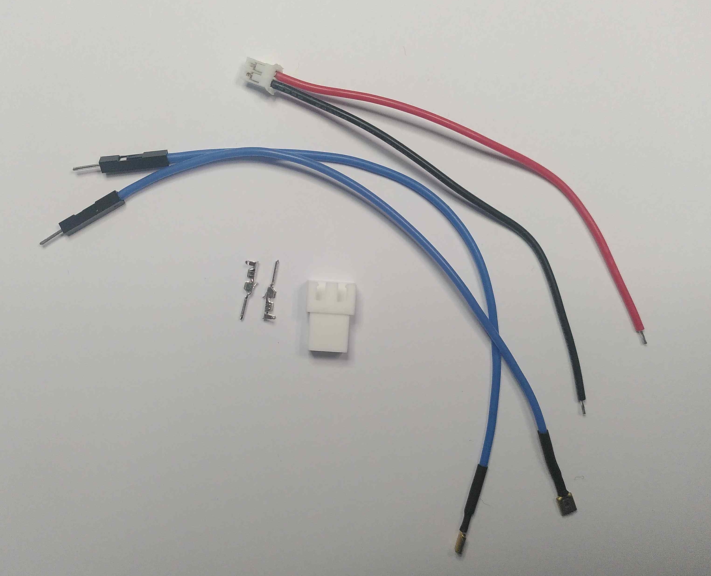
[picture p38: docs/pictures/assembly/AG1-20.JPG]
Fournitures pour câblage bouton


 - Couper un fil du switch au ras du connecteur dupont. Dénuder le fil, passer la gaine thermorétractable, puis souder au fil rouge du connecteur JST batterie. Protéger la soudure avec de la gaine thermorétractable.

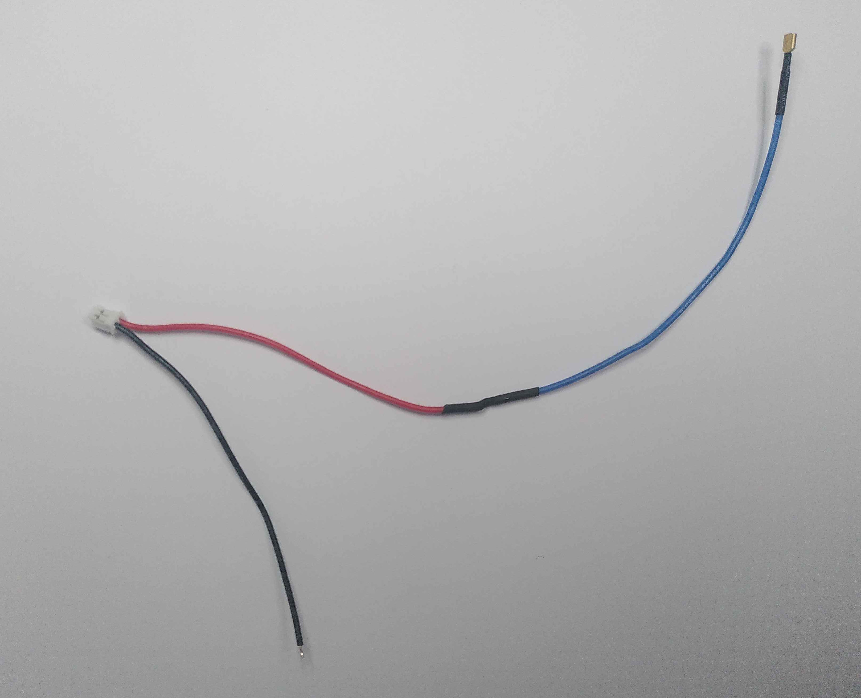
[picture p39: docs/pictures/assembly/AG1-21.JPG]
Soudure fil bouton au fil connecteur


 - Couper le second fil du switch au ras du connecteur dupont, le dénuder, et le sertir à une ferrure JST mâle. 
 - Faire de même avec le fil noir du connecteur batterie.

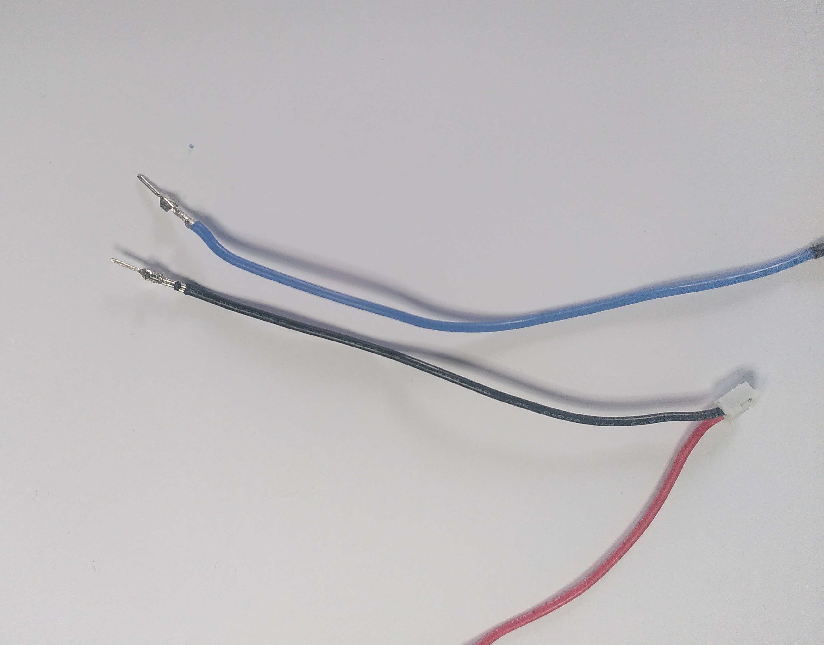
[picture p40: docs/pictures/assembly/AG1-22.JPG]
Sertir les fils du connecteur et du switch


 - Insérer ces ferrures dans le connecteur mâle 3 broches de manière à ce qu'une fois la batterie branché les deux fils noir soit face à face.

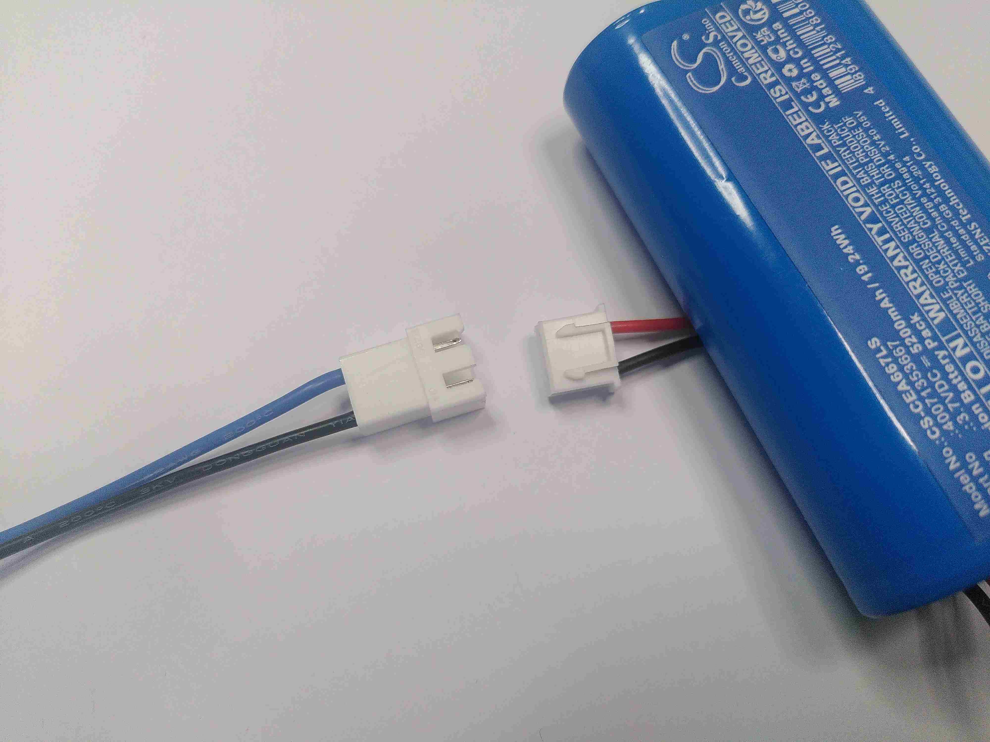
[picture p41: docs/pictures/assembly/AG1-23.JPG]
Implantation connectique
 

### 1.5 Connectique du voyant lumineux.
Le voyant lumineux blue robotics, ne requiert pas de résistance additionnelle. 
 - Rassembler, le voyant lumineux, un bloc JST mâle à 3 broches et 2 ferrures mâles.

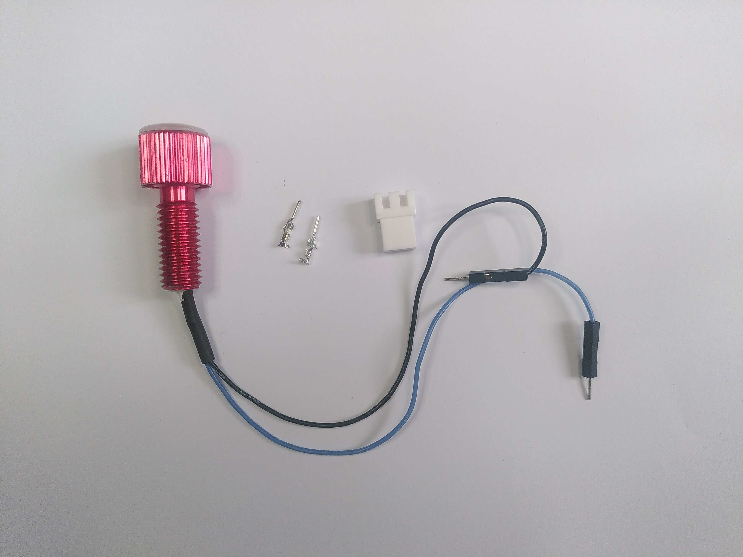
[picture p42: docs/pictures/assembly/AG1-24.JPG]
Fournitures pour voyant


 - Couper les deux fils du voyant lumineux, les dénuder et y sertir deux ferrures mâles. 

<section style="border: 2px solid red; padding: 20px; border-radius:20px; color: red;">
Attention avant de passer à l'étape suivante, il est important de placer le voyant sur la bride. En effet, le connecteur ne passera pas au travers de l'écrou.</section>

 - Rassembler le voyant lumineux, son joint torique, son écrou et une bride à 2 trous.

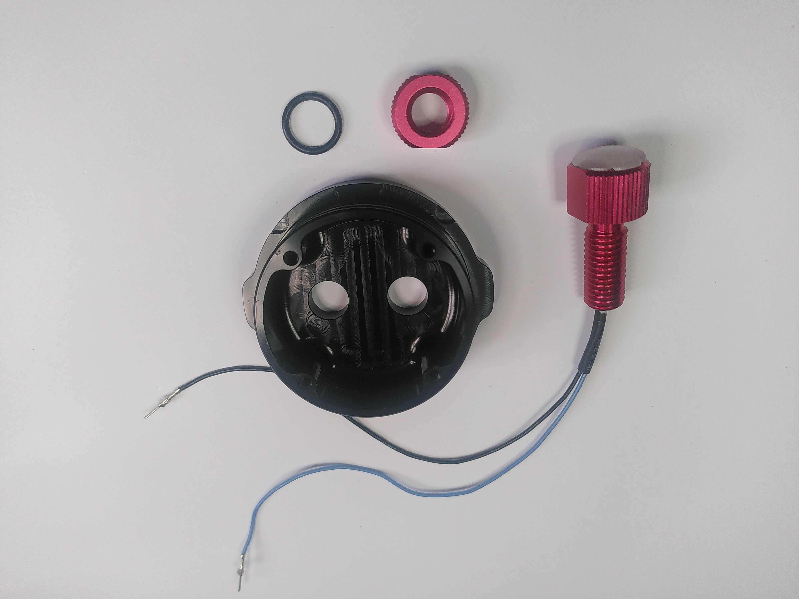
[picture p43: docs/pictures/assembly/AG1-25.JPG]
Plus la bride


 - Passer les fils du voyant lumineux dans le joint torique puis dans un trou de la bride et enfin dans l'écrou.

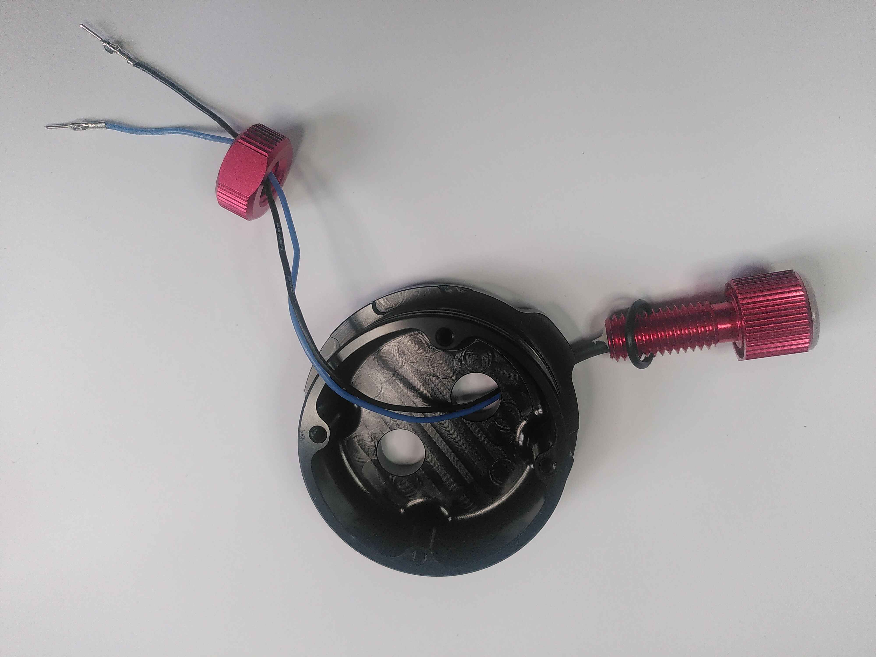
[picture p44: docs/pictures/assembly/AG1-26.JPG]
Enfilage


 - Ne pas graisser le joint qui est en compression. 
 - Serrer à la main pui à l'aide d'une clé.

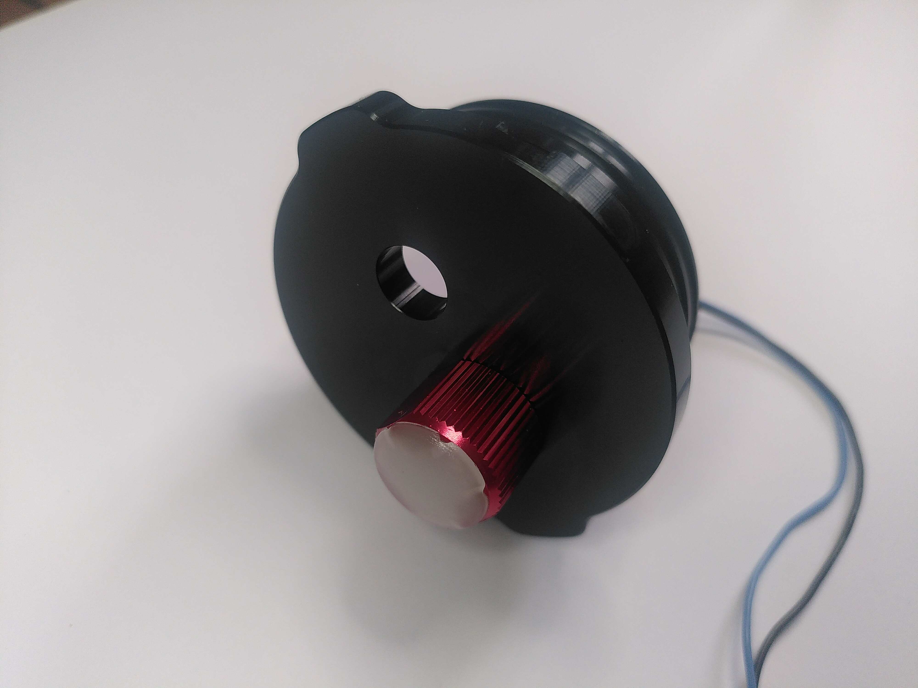
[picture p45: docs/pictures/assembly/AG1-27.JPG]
Serrage voyant


 - Insérer les ferrures dans un bloc connecteur JST 3 broches.

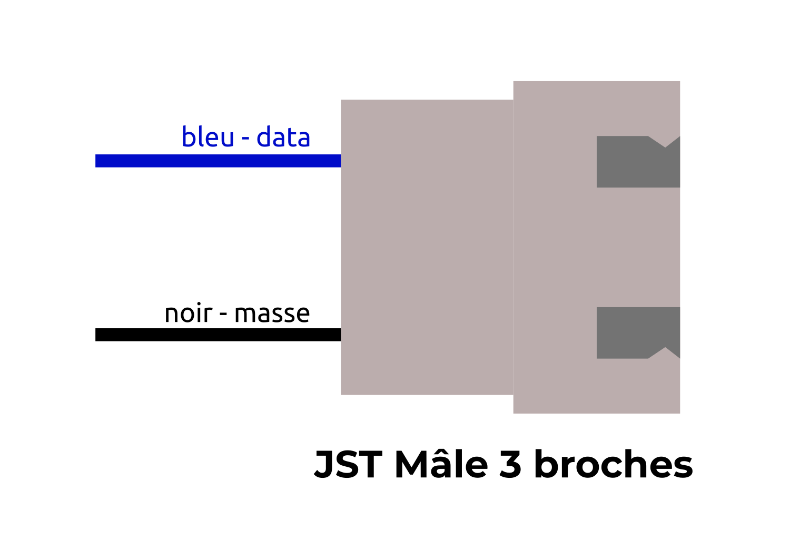
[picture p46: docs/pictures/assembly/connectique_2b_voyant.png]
Schèma d'implantation


 - Pour réaliser la rallonge du voyant lumineux, prendre : 4 ferrures JST femelles, 1 bloc JST femelle 3 broches et un autre de 2 broches, ainsi qu'un fil noir et bleu de 25cm environ. 
 - Dénuder et sertir chaque bout de fil. 
 - Insérer les ferrures dans les blocs en veillant aux polarités en se connectant à la carte d'une part et au voyant lumineux d'autre part. On peut torsader les fils.
 
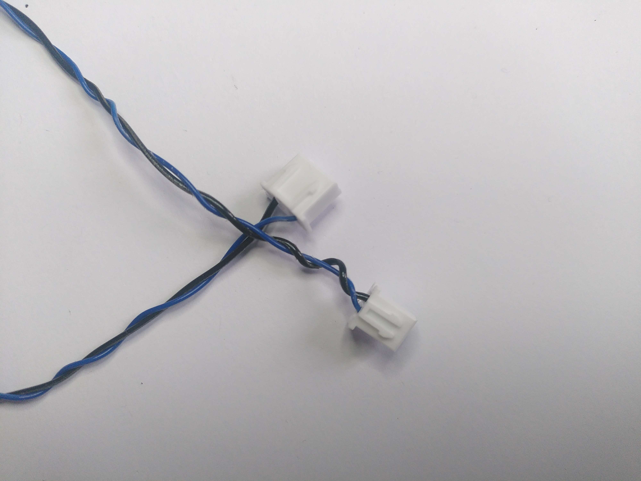
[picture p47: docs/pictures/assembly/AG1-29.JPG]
Rallonge, voyant lumineux


### 1.6 Rallonge du capteur de température
 - Pour réaliser la rallonge du capteur de température, couper 4 morceau de fil de 25cm environ (noir, rouge, vert et blanc). Rassembler aussi 8 ferrures JST femelle et 2 bloc connectiques femelles 4 broches.

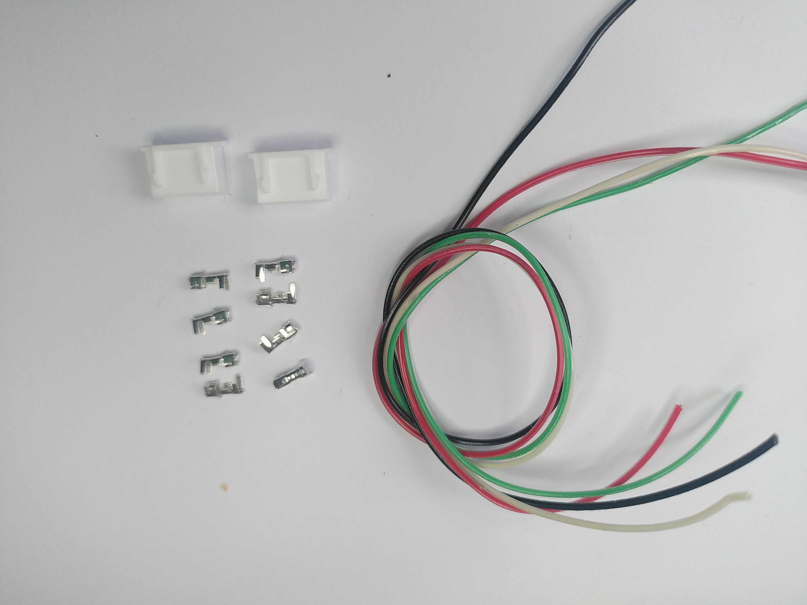
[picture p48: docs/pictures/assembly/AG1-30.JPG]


 - Insérer les ferrures dans un des blocs à 4 broches en suivant l'ordre de la photo.

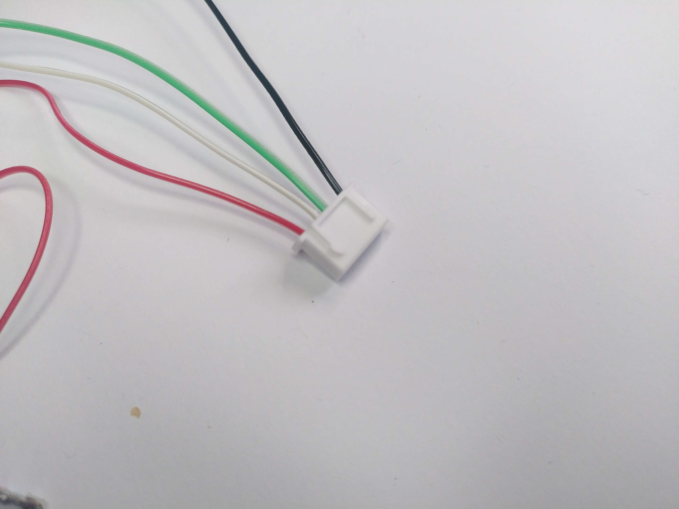
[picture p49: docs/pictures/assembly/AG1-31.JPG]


 - [Tresser les câbles en suivant ce tutoriel](https://youtu.be/7lTFIzm9BLY?si=LTKGTFpY72lfe2tC)
 - Insérer les ferrures opposés dans le secons bloc à 4 broches en suivant l'ordre de la photo.

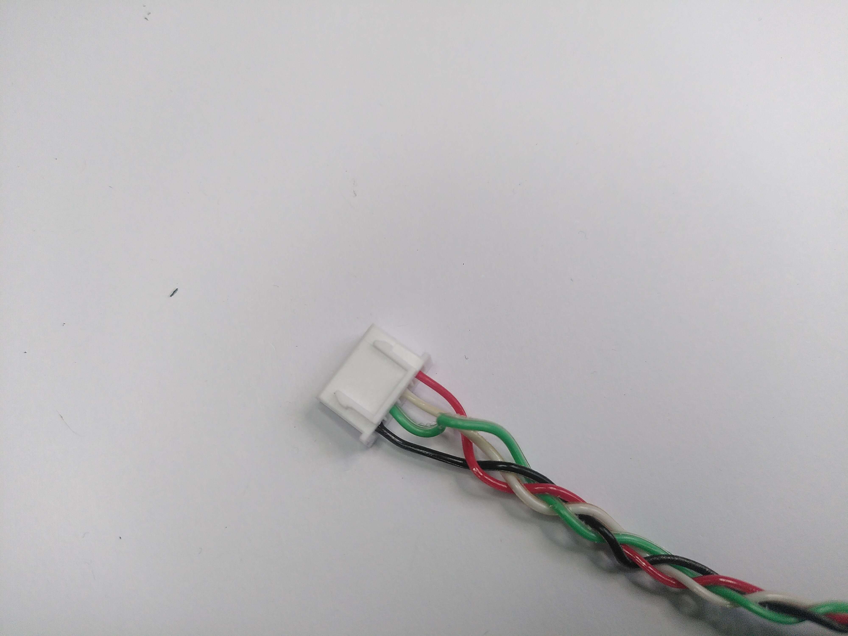
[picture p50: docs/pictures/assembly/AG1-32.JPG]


### 1.7 Rallonge de la carte microcontrôleur
 - Rassembler 5 fils (noir, rouge, blanc, vert et bleu) de 10 cm environ, 5 ferrures femelles JST, 1 bloc JST 5 broches femelles, 5 ferrures dupont femelles et deux bloc dupont 4 broches. 
 - Dénuder les fils. Sur chcun de fil, sertir une ferrure femelle JST d'un bout et de l'autre une ferrure dupont femelle.
 - Insérer les ferrures JST dans le bloc JST à 5 broches dans le sens indiqué.

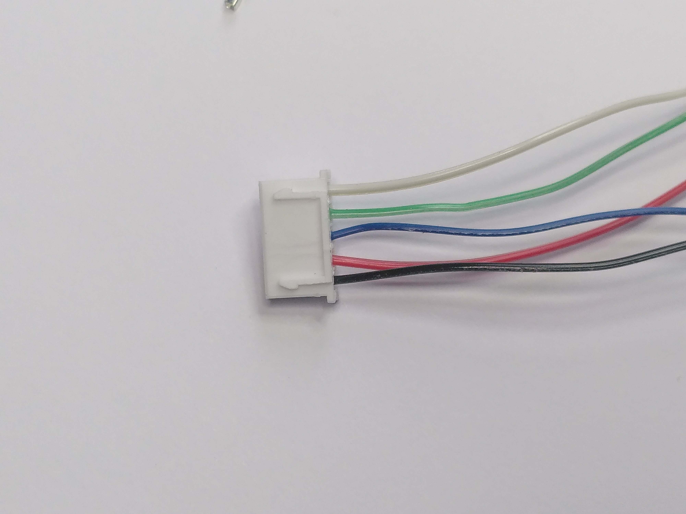
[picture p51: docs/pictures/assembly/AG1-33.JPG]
Connecteur JST, carte micro controleur


 - Insérer les ferrures dupont dans les bloc Dupont 4 broches dans le sens indiqué.
 
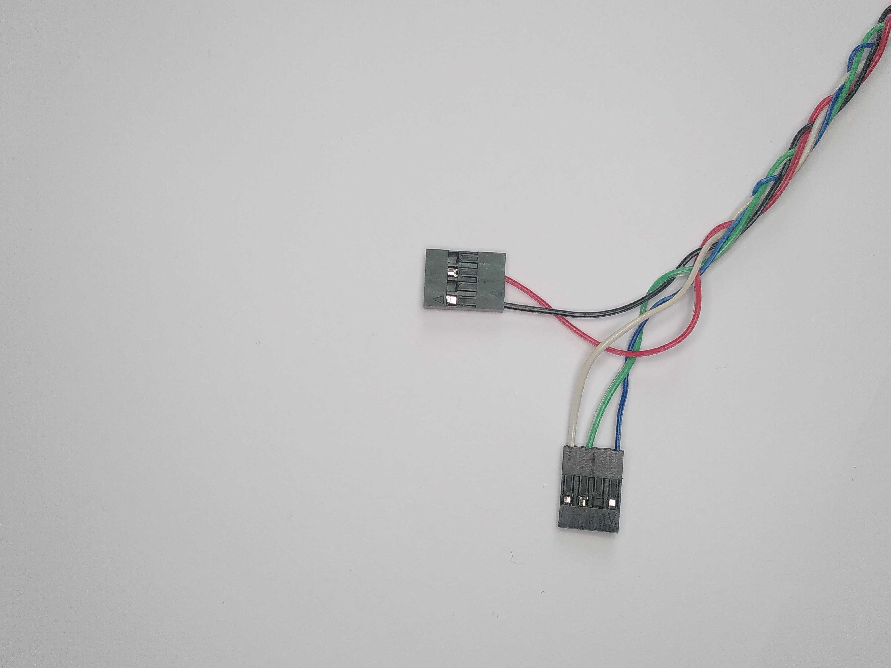
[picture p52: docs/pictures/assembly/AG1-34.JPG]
Connecteur Dupont, carte micro controleur


### 1.8 Fixation du switch
 - Rassembler tous les composants du switch étanche. C'est à dire, le pénétrateur, le bouton rotatif, l'écrou et 3 joints dont un est plus épais que les deux autres. 

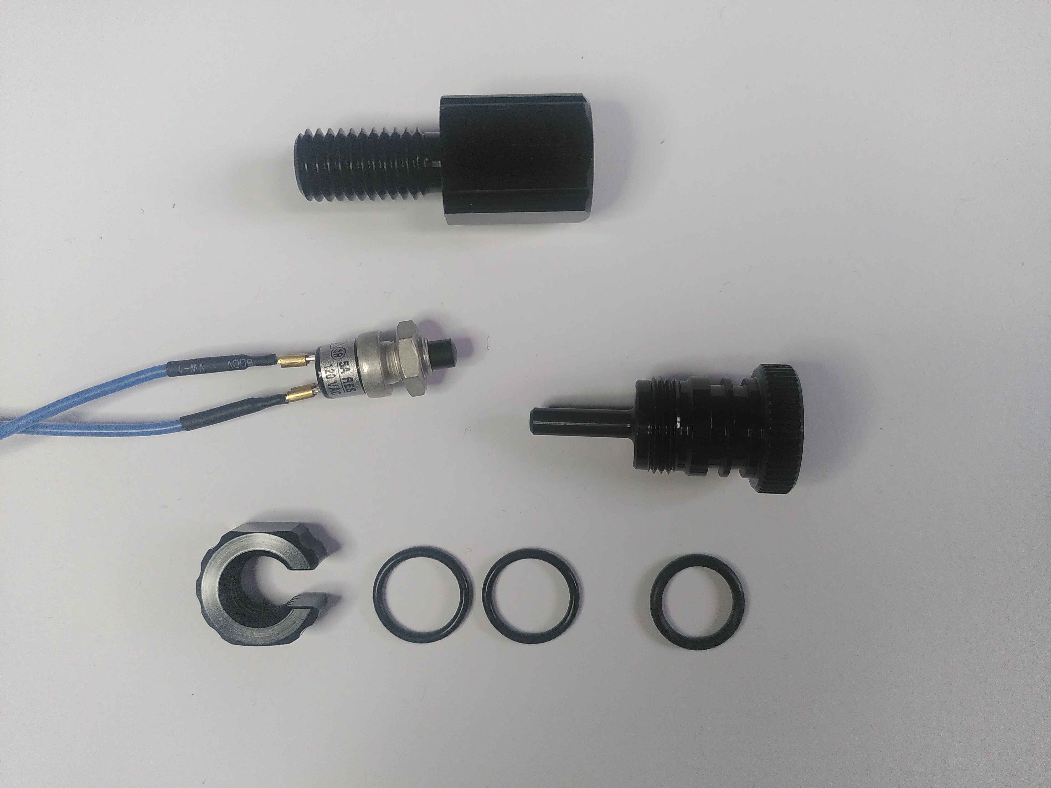
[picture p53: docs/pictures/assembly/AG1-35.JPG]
Rassembler pour switch


 - Insérer la vis du pénétrateur dans le joint le plus épais de trois. Insérer le pénétrateur dans le second trou de la bride où se trouve déjà le voyant lumineux. Le joint doit se trouver du coté extérieur.

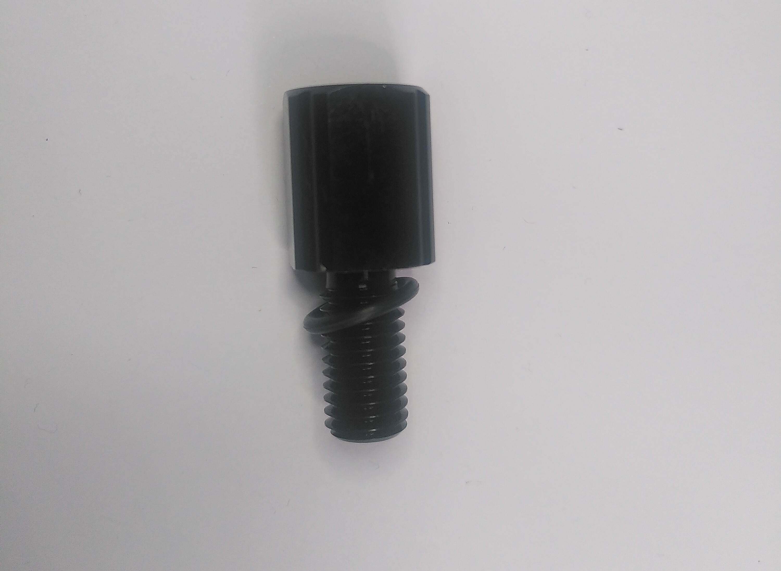
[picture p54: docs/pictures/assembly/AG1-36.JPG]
Insertion joint torique


 - Serrer à la main puis à l'aide d'une clé. 
 - Retirer l'écrou (argenté) se trouvant sur le bouton poussoir.
 - Visser le bouton poussoir au bout (coté intérieur) du pénétrateur switch.
 
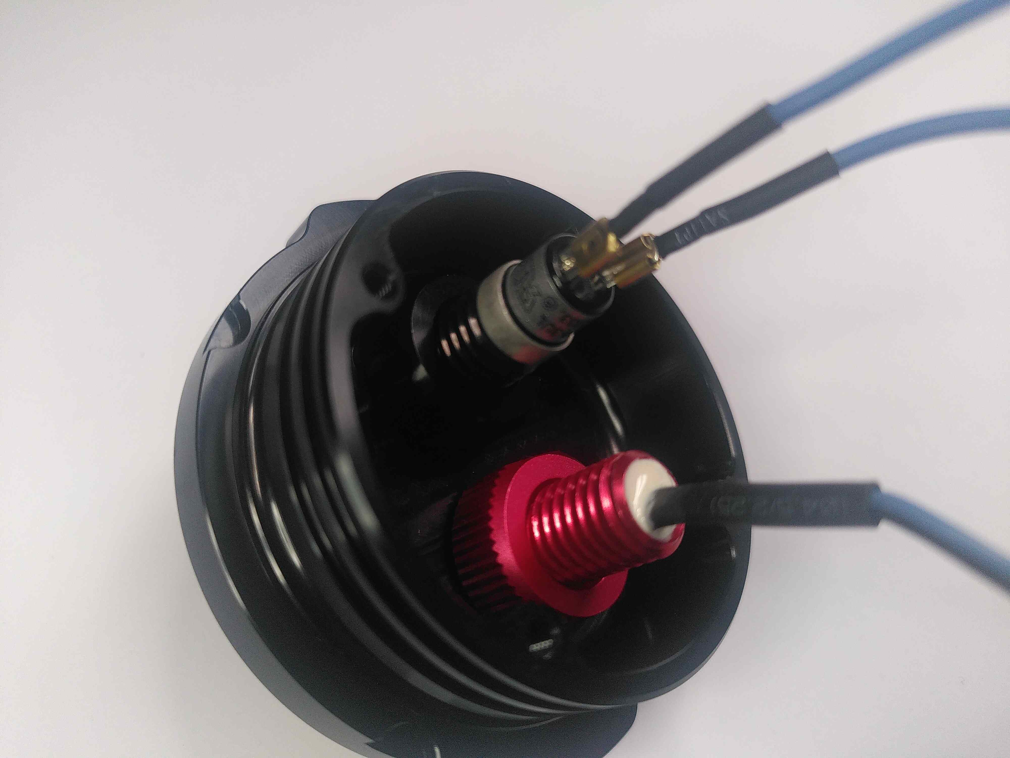
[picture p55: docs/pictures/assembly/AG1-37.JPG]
serrer et positionnement du bouton poussoir


 - Les deux derniers joints doivent être graissés avec de la graisse silicone.
 - En déposer une légère pointe sur le doit et frotter chacun des joints délicatement. Il ne doit rester aucune goutte.
 - Une fois graissé insérer ces joints dans les rainures du bouton tournant. 

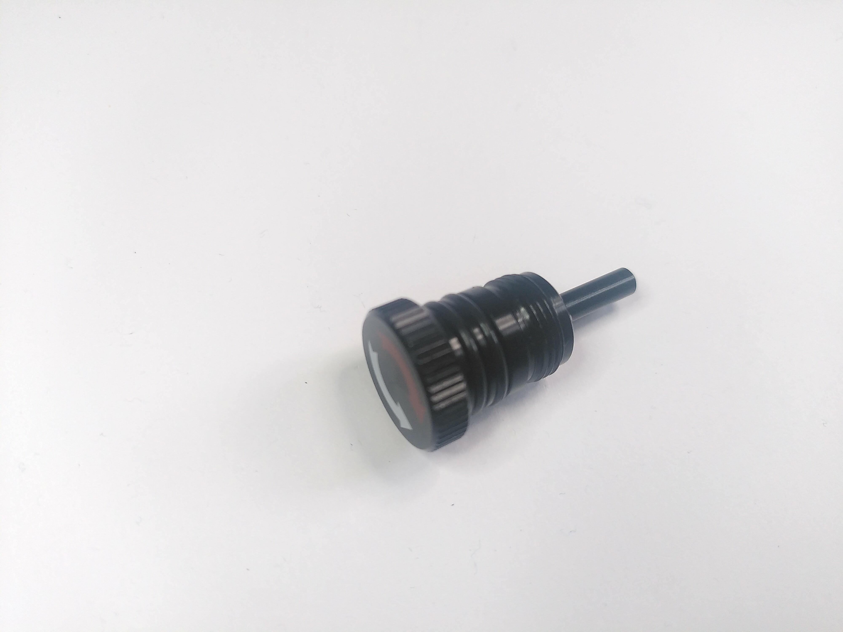
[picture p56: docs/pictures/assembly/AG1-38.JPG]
Positionnement joints sur bouton


 - Visser le bouton dans le pénétrateur. Si nécéssaire ajouter une pointe de graisse silicone.

Visser le bouton dans le pénétrateur

 - A l'aide d'un multimètre tester le bon fonctionnement du Switch.

<section style="border: 2px solid red; padding: 20px; border-radius:20px; color: red;">
Attention ! Laisser le bouton ouvert (le courant ne peut passer) pour les étapes suivantes et surtout avant de brancher la batterie au reste du circuit.</section>

### 1.9 Installation de la mise à l'air libre
 - Rassembler le bouchon de mise àl'aire libre (ou vent) et tous ces accessoires ( 1 pénétrateur, 3 joints toriques, 1 écrou.)

## 2. Assemblage final
### 2.1 Agencement intérieur
 - Rassembler la bride qui acueillera le capteur de température et ses joints toriques.

<section style="border: 1px solid green; padding: 20px; border-radius:20px; color: green;">
ⓘ Info ! Dans notre cas, une de nos deux brides étaint composé d'une flange à insérer dans le tube et d'une plaque d'aluminium percé que l'on vissait sur la flange. Les dernières versions commercialisés sont faites d'un seul bloc.</section>
 - Graisser à l'aide de graisse silicone au doigt les deux joints.
 Graisser les joints
 - Les insérer dans leurs gorges respectives. 
 - Rassembler la rondelle R1, 4 vis M3*6mm et la bride contenant le capteur de température.
 - Visser R1 sur la bride comportant le capteur de température. 
  Rassembler la rondelle R1 et la bride
 - Assembler le support S1 avec la rondelle R1 et la R2, de manière à positionner l'encoche arrondi de S1 du coté de R1. 
 Assembler S1 avec R1 et R2
 - Placer la batterie sur son support S1 au moyens de deux colliers de serrages. 
 Placer la batterie
 - Ces dernier devront passer dans les encoches sur le coté du support S1 afin de ne pas gêner l'insertion de l'ensemble dans le tube. 
 - Passer les câble de la batterie et du capteur de température au travers de R2. 
 - Rassembler le support S2, la carte adafruit addlogger, la carte RTC (les désolidariser) et 4 vis M2,5*5mm. 
 - Visser la carte RTC sur le support S1 en respectant le sens sur la photo. 
 Assembler S2 avec la carte adafruit addlogger
 - En dessous de la carte RTC brancher la carte adafruit addalogger M0.
  Brancher la carte adafruit addalogger sous la carte RTC
 - Rassembler la carte secondaire et 2 vis M3*5mm. 
 - Visser la carte secondaire sur le support S1 comme présenté sur la photo ci-dessous. 
  Visser la carte secondaire sur le support S1
 - Positionner les rondelles R3 et R4 à chaque extrémité de S2. R3 viendra coté carte secondaire et R4 coté circuit RTC.

### 2.2 Branchements
 - A l'aide du câble fabriqué à 4 fils, relier le capteur de température au connecteur JST 4 broches de la carte secondaire. 
 - Faire de même avec la rallonge du voyant lumineux qui permettra de relier le voyant au bloc 2 broches de la carte secondaire.
 - Connecter le câble (5 fils), connecteur JST femelle sur le conecteur 5 broches de la carte secondaire. 
Branchement connecteurs carte secondaire
 - Brancher le câble de la batterie, premièrement sur le switch puis sur la carte adafruit addaloger M0 puis connecter la batterie. 
Branchement batterie
 - Connecter les autres extrémités sur les broches du RTC comme indiqué sur le schéma ci-dessous.
Branchement carte secondaire
 - Insérer la pile bouton du RTC dans son logement. 
Insérer pile bouton du RTC

### 2.3 Fermeture du tube
 - Insérer le tout dans le tube.
 - Enfoncer la bride contenant le capteur de température d'un bout. 
 - Veiller à ce que l'encoche soit placé dans l'encoche du tube PMMA. 

<section style="border: 2px solid red; padding: 20px; border-radius:20px; color: red;">
Attention ! Afin de fermer un tube étanche : 
<li>Ne pas forcer, graisser les joints légèrement et sans surplus.</li>
<li>Veiller aux éléments fragiles comme le capteur de température</li>
<li>Ouvrir le bouchon de la mise à l'air libre pour ne pas créer de surpression</li>
</section>
 - Fermer la bride du coté opposé. 
 - Rassembler les deux tiges en plastiques souple, les rondelles de blocages et les 2 vis de serrage fourni avec les brides.
Visser la carte secondaire sur le support S1 
 - Monter ces goupilles souples en plaçant la rondelle à l'extrémité de chacune de tiges de plastique souple. 
 - Insérer ces goupilles entre le tube et la bride pour bloquer l'ouverture du tube. 

### 2.4 Points d'accrochages
 - Rassembler de la chambre à air de vélo usagé, 2 colliers de serrages et du bout de 4 mm.
 - A chaque extrémité, du tube, positionner un collier de serrage sur une bande de chambre à air de vélo. 
 - Y coincer un morceau de bout de manière à faire une boucle.  
 - Recouvrir le tout de chaterton.

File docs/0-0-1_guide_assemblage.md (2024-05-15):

# Guide d'assemblage

## 1/ Préparations, câblages et soudures
### 1.1 Connectique du capteur de température

 - Rassembler le capteur de température (et ses accessoires, le joint et l'écrou), un bloc connectique mâle JST 4 voies (4P Plug Housing), 4 ferrures mâles JST à sertir, ainsi qu'une bride à 2 perforations (ou une plaque alu deux perforations). 
Photo montrant les éléments nécessaires
 - A l'aide d'une pince coupante, sectionner le connecteur du capteur déjà en place. Veiller à couper au plus proche du connecteur afin de conserver un maximum de fil.
 - Dénuder chacun des fils au moyen d'une pince à dénuder. 
 - Sertir au bout de chaque fil une ferrure mâle.

Photo montrant le capteur de température et les 4 fils sertis

<section style="border: 2px solid red; padding: 20px; border-radius:20px; color: red;">
Attention ! Avant de positionner les ferrures dans le bloc connecteur JST, il faudra passer le capteur dans un trou de la bride. Ceci ne pouvant pas être fait après car le connecteur ne passe pas dans la perforation de la bride. </section>

 - Positionner le joint torique du coté extérieur, puis passer le pénétrateur dans la bride, pour enfin serrer avec l'écrou à la main puis à l'aide d'une clé. 

Photo montrant le capteur de température et les 4 fils sertis

 - Enfoncer chacun des fil dans le connecteur JST. En suivant le schéma ci-dessous. 

Schèma d'implantation des fils du capteur.
Photo montrant le capteur de température et le connecteur JST en place

### 1.2 Préparation du micro-controleur 

 - Rassembler l'horloge (la carte RTC), et 2 lignes de broches dupont mâle (1* 16 broches et 1* 12 broches).

Photo montrant l'horloge RTC au coté des deux connecteurs duponts mâle.

 - Souder ces deux connecteurs duponts comme suit. 

<section style="border: 2px solid red; padding: 20px; border-radius:20px; color: red;"><b>Attention</b> à veiller à :
<li>Souder les broches sur les emplacements externes</li>
<li>Positionner les broches à l'opposé de l'emplacement de la pile. </li>
<li>Souder les broches les plus courtes.</li>
<li>Veiller à maintenir les broches bien perpendiculaire à la plaque. </li>
</section>

On a soudé les deux broches duponts sur la carte d'horloge RTC

 - Rassembler l'horloge RTC qui viens d'être soudé ainsi que deux nouvelles lignes de broches (1* 16 broches et 1* 11 broches).

La carte RTC et des broches

 - Souder ces broches à l'opposé des broches installé à l'étape précédente. 

On a soudé les deux nouvelles broches duponts sur la carte d'horloge RTC

 - Rassembler le microcontrôleur (Adafruit MO), ainsi que deux lignes de broches dupont femelles (1* 16 broches et 1* 12 broches).
 
La carte Adafruit M0 et des broches femelles

 - Souder ces broches en veillant au sens. Le coté femelle doit se retrouver au dessus de la carte.
 - C'est ici que viendra se brancher l'horloge RTC. 

On a soudé les deux broches duponts femelles sur la carte Adafruit M0

 - Enfin, assembler les deux cartes électronique l'une sur l'autre. 
 - L'horloge RTC viendra donc au dessu du micro-contrôleur. 

Assemblage des deux cartes électroniques

### 1.3 Assemblage du circuit secondaire
Le circuit secondaire, va permettre dans un premier temps de faciliter les connexions entre capteurs et voyants. Il permet aussi d'ajouter des composants nécéssaires comme les résistances de tirages sur le capteur qui communique suivant le protocole I2C.

 - Rassembler, une plaque de prototypage adafruit, trois connecteurs JST mâles à souder 5, 4 et 2 broches, 2 résistances de 10 kohm, du fil électrique à souder.

Fournitures pour soudure sur carte secondaire 

 - Prendre la plaque de prototypage dans le sens où les lettres des colonnes demeurent dans le bon sens pour la lecture.
 - Souder les 3 connecteurs JST femelles en suivant le plan ci-dessous. Le connecteur 5 broches de G1 à G5, le connecteur de 2 broches de G8 à G9 et le connecteur à 4 broches entre G12 et G15.

Implantation des 3 connecteurs m^les sur la carte secondaire

 - Au moyen de trois morceaux de fil (de préférence noir) relier chaque ligne (1, 8 et 12) à la colonne de masse symbolisé par un "-".

Implantation des ponts de masses

 - Souder un pont (fil de couleur rouge) entre la ligne 2 et la colonne "+".

Implantation fil de + 

 - Souder un pont (fil bleu) entre les ligens 3 et 9. Il s'agit du fil de donnée logique pour contrôler le voyant lumineux. 

Implantation fil de data bleu

 - Souder un pont (fil vert) entre les lignes 4 et 13. Il s'agit du SCL, l'horloge pour la lecture du capteur de température. 
 - Souder un pont (fil blanc) entre les lignes 5 et 14. Il s'agit du SDA, le fil de datas pour la lecture du capteur de température. 

Implantation fil vert SCL et blanc SDA

 - Souder les deux résistances de 10kohm entre la ligne 13 et le "+" et la seconde entre la ligne 14 et le "+".
 - Se servir d'une des patte de résistance coupé pour faire un pont entre la ligne 15 et la colonne "+".

Implantation des résistances et de l'alimentation du capteur de température 
 
### 1.4 Connectiques de la batterie
 - Couper un fil du connecteur de la batterie, le dénuder et le souder à un autre fil de même couleur pour le rallonger de 25cm environ. 
 - Isoler la soudure au moyen de gaine thermorétractable. 
 - Faire de même pour rallonger le second fil. 

<section style="border: 2px solid red; padding: 20px; border-radius:20px; color: red;">Attention pendant cette manipulation à ce qu'aucun fil ne se touche pour éviter un court-circuit.</section>

Rallonge des fils de la batterie

 - Rassembler, la batterie, un connecteur femelle JST à 3 broches (je n'avais pas de 2 broches dans ma boite) et 3 ferrures JST femelles.
 - Dénuder un fil de la batterie, et y sertir une ferrure femelle. 
 - Insérer cette ferrure dans le bloc 3 broches JST mâle. Veiller à respecter le même sens que sur la photo.
 - Faire de même avec le second fil et l'insérer dans le bloc JST à l'opposé du premier.

Implantation du connecteur JST batterie

 - Rassembler, les fils du boutons (switch) étanche, un connecteur JST de batterie, un connecteur JST mâle 3 broches et 2 ferrures mâle.

Fournitures pour câblage bouton

 - Couper un fil du switch au ras du connecteur dupont. Dénuder le fil et le souder au fil rouge du connecteur JST batterie. Protéger la soudure avec de la gaine thermorétractable.

Soudure fil bouton au fil connecteur

 - Couper le second fil du switch au ras du connecteur dupont, le dénuder, et le sertir à une ferrure JST mâle. 
 - Faire de même avec le fil noir du connecteur batterie.

Sertir les fils du connecteur et du switch

 - Insérer ces ferrures dans le connecteur mâle 3 broches de manière à ce qu'une fois la batterie branché les deux fils noir soit face à face.

Implantation connectique 

### 1.5 Connectique du voyant lumineux.
Le voyant lumineux blue robotics, ne requiert pas de résistance additionnelle. 
 - Rassembler, le voyant lumineux, un bloc JST mâle à 3 broches et 2 ferrures mâles.

Fournitures pour voyant

 - Couper les deux fils du voyant lumineux, les dénuder et y sertir deux ferrures mâles. 

<section style="border: 2px solid red; padding: 20px; border-radius:20px; color: red;">
Attention avant de passer à l'étape suivante, il est important de placer le voyant sur la bride. En effet, le connecteur ne passera pas au travers de l'écrou.</section>

 - Rassembler le voyant lumineux, son joint torique, son écrou et une bride à 2 trous.

Plus la bride

 - Passer les fils du voyant lumineux dans le joint torique puis dans un trou de la bride et enfin dans l'écrou.

Enfilage

 - Ne pas graisser le joint qui est en compression. 
 - Serrer à la main pui à l'aide d'une clé.

Serrage voyant

 - Insérer les ferrures dans un bloc connecteur JST 3 broches.

Schèma d'implantation

 - Pour réaliser la rallonge du voyant lumineux, prendre : 4 ferrures JST femelles, 1 bloc JST femelle 3 broches et un autre de 2 broches, ainsi qu'un fil noir et bleu de 25cm environ. 
 - Dénuder et sertir chaque bout de fil. 
 - Insérer les ferrures dans les blocs en veillant aux polarités en se connectant à la carte d'une part et au voyant lumineux d'autre part. On peut torsader les fils.
 
Rallonge, voyant lumineux

### 1.6 Rallonge du capteur de température
 - Pour réaliser la rallonge du capteur de température, couper 4 morceau de fil de 25cm environ (noir, rouge, vert et blanc). Rassembler aussi 8 ferrures JST femelle et 2 bloc connectiques femelles 4 broches.

Rallonge, capteur

 - Insérer les ferrures dans un des blocs à 4 broches en suivant l'ordre de la photo.

Rallonge, capteur

 - [Tresser les câbles en suivant ce tutoriel](https://youtu.be/7lTFIzm9BLY?si=LTKGTFpY72lfe2tC)
 - Insérer les ferrures opposés dans le secons bloc à 4 broches en suivant l'ordre de la photo.

Rallonge, capteur

### 1.7 Rallonge de la carte microcontrôleur
 - Rassembler 5 fils (noir, rouge, blanc, vert et bleu) de 10 cm environ, 5 ferrures femelles JST, 1 bloc JST 5 broches femelles, 5 ferrures dupont femelles et deux bloc dupont 4 broches. 
 - Dénuder les fils. Sur chcun de fil, sertir une ferrure femelle JST d'un bout et de l'autre une ferrure dupont femelle.
 - Insérer les ferrures JST dans le bloc JST à 5 broches dans le sens indiqué.

Connecteur JST, carte micro controleur

 - Insérer les ferrures dupont dans les bloc Dupont 4 broches dans le sens indiqué.
 
Connecteur Dupont, carte micro controleur

### 1.8 Fixation du switch
 - Rassembler tous les composants du switch étanche. C'est à dire, le pénétrateur, le bouton rotatif, l'écrou et 3 joints dont un est plus épais que les deux autres. 

Rassembler pour switch

 - Insérer la vis du pénétrateur dans le joint le plus épais de trois. Insérer le pénétrateur dans le second trou de la bride où se trouve déjà le voyant lumineux. Le joint doit se trouver du coté extérieur.

Insertion joint torique

 - Serrer à la main puis à l'aide d'une clé. 
 - Retirer l'écrou (argenté) se trouvant sur le bouton poussoir.
 - Visser le bouton poussoir au bout (coté intérieur) du pénétrateur switch.
 
serrer et positionnement du bouton poussoir

 - Les deux derniers joints doivent être graissés avec de la graisse silicone.
 - En déposer une légère pointe sur le doit et frotter chacun des joints délicatement. Il ne doit rester aucune goutte.
 - Une fois graissé insérer ces joints dans les rainures du bouton tournant. 

Positionnement joints sur bouton

 - Visser le bouton dans le pénétrateur. Si nécéssaire ajouter une pointe de graisse silicone.

Visser le bouton dans le pénétrateur

 - A l'aide d'un multimètre tester le bon fonctionnement du Switch.

<section style="border: 2px solid red; padding: 20px; border-radius:20px; color: red;">
Attention ! Laisser le bouton ouvert (le courant ne peut passer) pour les étapes suivantes et surtout avant de brancher la batterie au reste du circuit.</section>

## 1.9 Installation de la mise à l'air libre
 - Rassembler le bouchon de mise àl'aire libre (ou vent) et tous ces accessoires ( 1 pénétrateur, 3 joints toriques, 1 écrou.)

## 2. Assemblage final
### 2.1 Agencement intérieur
 - Rassembler la bride qui acuillera le capteur de température et ses joints toriques.

<section style="border: 1px solid green; padding: 20px; border-radius:20px; color: green;">
ⓘ Info ! Dans notre cas, une de nos deux brides étaint composé d'une flange à insérer dans le tube et d'une plaque d'aluminium percé que l'on vissait sur la flange. Les dernières versions commercialisés sont faites d'un seul bloc.</section>
 - Graisser à l'aide de graisse silicone au doigt les deux joints.
 - Les insérer dans leurs gorges respectives. 
 - Rassembler la rondelle R1, 4 vis M3*6mm et la bride contenant le capteur de température.
 - Visser R1 sur la bride comportant le capteur de température. 
 - Assembler le support S1 avec la rondelle R1 et la R2, de manière à positionner l'encoche arrondi de S1 du coté de R1. 
 - Placer la batterie sur son support S1 au moyens de deux colliers de serrages. 
 - Ces dernier devront passer dans les encoches sur le coté du support S1 afin de ne pas gêner l'insertion de l'ensemble dans le tube. 
 - Passer les câble de la batterie et du capteur de température au travers de R2. 
 - Rassembler le support S2, la carte adafruit addlogger, la carte RTC (les désolidariser) et 4 vis M2,5*5mm. 
 - Visser la carte RTC sur le support S1 en respectant lesens sur la photo. 
 - En dessous de la carte RTC brancher la carte adafruit addaloger M0.
 - Rassembler la carte secondaire et 2 vis M3*5mm. 
 - Visser la carte secondaire sur le support S1 comme présenté sur la photo ci-dessous. 
 - Positionner les rondelles R3 et R4 à chaque extrémité de S2. R3 viendra coté carte secondaire et R4 coté circuit RTC.

### 2.2 Branchements
 - A l'aide du câble fabriqué à 4 fils, relier le capteur de température au connecteur JST 4 broches de la carte secondaire. 
 - Faire de même avec la rallonge du voyant lumineux qui permettra de relier le voyant au bloc 2 broches de la carte secondaire. 
 - Brancher le câble de la batterie, premièrement sur le switch puis sur la carte adafruit addaloger M0 puis connecter la batterie. 
 - Connecter le câble (5 fils), connecteur JST femelle sur le conecteur 5 broches de la carte secondaire. 
 - Connecter les autres extrémités sur les broches du RTC comme indiqué sur le schéma ci-dessous. 

### 2.3 Fermeture du tube
 - Insérer le tout dans le tube.
 - Enfoncer la bride contenant le capteur de température d'un bout. 
 - Veiller à ce que l'encoche soit placé dans l'encoche du tube PMMA. 

<section style="border: 2px solid red; padding: 20px; border-radius:20px; color: red;">
Attention ! Afin de fermer un tube étanche : 
<li>Ne pas forcer, graisser les joints légèrement et sans surplus.</li>
<li>Veiller aux éléments fragiles comme le capteur de température</li>
<li>Ouvrir le bouchon de la mise à l'air libre pour ne pas créer de surpression</li>
</section>
 - Fermer la bride du coté opposé. 

### 2.4 Points d'accrochages
 - Chambr à air, colliers de serrages et bout.

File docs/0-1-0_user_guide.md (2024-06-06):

# II. Guide d'utilisation

En cours de rédaction !

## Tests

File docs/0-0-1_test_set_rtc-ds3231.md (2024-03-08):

# 0-0-1 -- Test de l'horloge RTC

## 1/ Introduction
Dans cette étape qui viens après l'essai du capteur de température, je vais détailler comment j'ai ajouté les données de temps (Date et heure) au moyen d'un shield RTC. 

Le RTC (Real Time Clock) est un circuit qui au moyen d'une pile peut garder en mémoire l'heure. Ainsi lorsque l'on rallumera la sonde, elle sera toujours à l'heure. Dans la limite de la pile évidemment. 
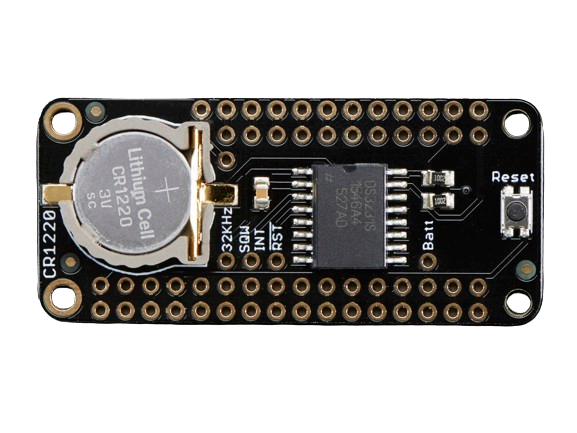
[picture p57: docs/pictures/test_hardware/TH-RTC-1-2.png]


## 2/ Matériel et fournitures
### 2.1 Fournitures
 - Adafruit adalogger M0 ;
 - Module RTC (DS3231 RTC Featherwing) ;
 - Pile bouton CR1220 ;

### 2.2 Matériel
 - PC sur windows (de préférence) ou linux ;
 - Câble USB vers micro USB ;
 - Logiciel [Arduino IDE](https://www.arduino.cc/en/software) ;

## 3/ Réalisation
### 3.1 Hardware
Pour connecter la carte Adafruit M0 au shield RTC, il est nécéssaire de souder dans un premier temps des connecteurs duponts. **Pour cela, se référer au guide d'assemblage** afin d'éviter de devoir déssouder les broches pour fabriquer la sonde. 

 - Connecter l'Adafruit et le shield RTC en les superposant. 
 - Installer la pile bouton CR1220 dans l'emplacement prévu à cet effet. Positionner la face gravé vers le haut. 
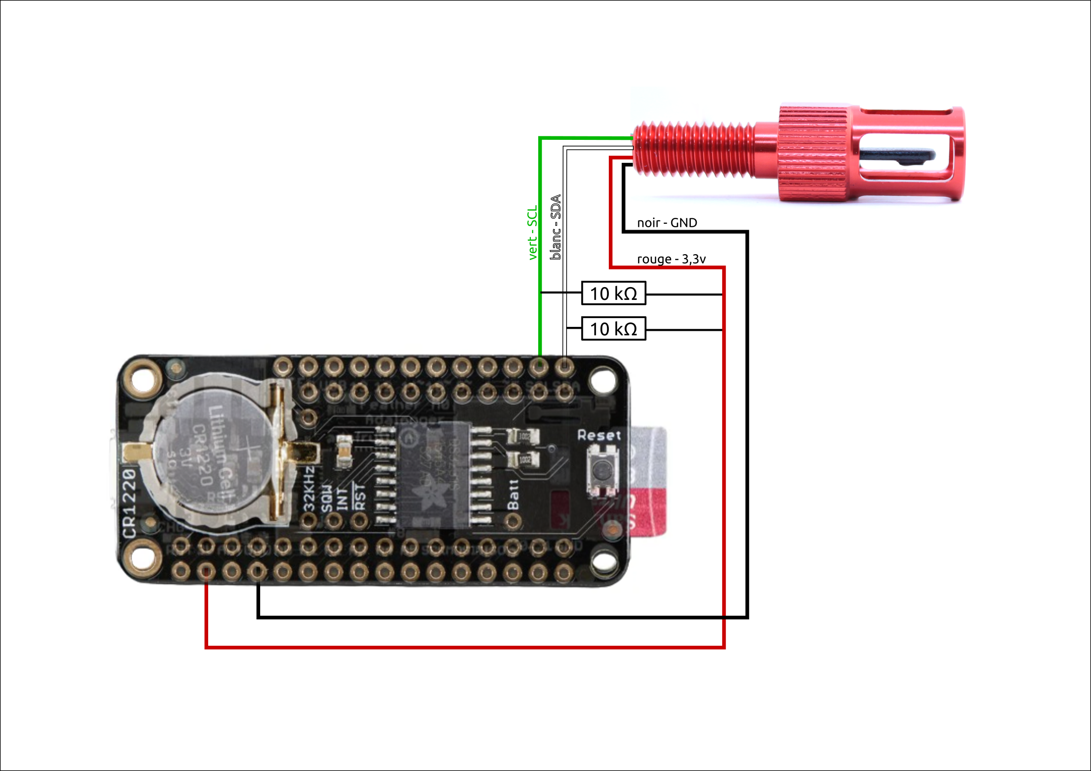
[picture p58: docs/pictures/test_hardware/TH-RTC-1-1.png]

*Ce visuel tente de montrer les deux cartes positionés l'une sur l'autre.*

### 3.2 Software
#### 3.2.1 Mise à l'heure

Avant toute chose, il faut initialiser l'horloge, en lui entrant la bonne heure. La question qui se pose est qu'elle heure ? 
 - **L'heure locale ?** : Dans ce cas si la sonde voyage, il peut-être difficile de s'y retrouver. 
 - **Ou l'heure universelle (UTC) ? **: Mais une telle initialisation demande une manipulation particulière. 

#### 3.2.2 Programme qui marche
Ce programme en C++ fonctionne avec l'horloge et le capteur de température.
Toutes les secondes, le programme renvoi dans le moniteur série la date, l'heure et la  
```c++
//Date and time functions using a DS3231 RTC connected via I2C and Wire lib
#include <Wire.h>
#include "RTClib.h"

//Librairie pour lire le capteur de température
#include "TSYS01.h"

TSYS01 sensor;
RTC_DS3231 rtc;
//RTC_PCF8523 rtc; //décommenter si utilisation de ce RTC

// Définition des variables
float temp;

void setup() {

  Serial.begin(9600);

  if (! rtc.begin()) {
    Serial.println("Couldn't find RTC");
    while (1);
  }
  //Initialize real-time clock
  if (rtc.lostPower()) {

    //reset RTC with time when code was compiled if RTC loses power
    Serial.println("RTC lost power, lets set the time!");
    rtc.adjust(DateTime(F(__DATE__), F(__TIME__)));
  }

  delay(250);   // Wait a quarter second to continue.
  
  Serial.println("Starting mesurements");
  
  Wire.begin();

  sensor.init();

}

void loop() {

 DateTime now = rtc.now(); //check RTC
    char dateTimeString[40];
    get_date_time_string(dateTimeString, now);
    
  sensor.read();
  //output readings to serial
  Serial.print("Time: ");
  Serial.print(dateTimeString);
  Serial.print(" , ");
  Serial.print("Temperature: ");
  Serial.print(sensor.temperature()); 
  Serial.println("°C");

  delay(1000);
}

void get_date_time_string(char* outStr, DateTime date) {
  // outputs the date as a date time string,
  sprintf(outStr, "%02d/%02d/%02d,%02d:%02d:%02d", date.year(), date.month(), date.day(), date.hour(), date.minute(), date.second());
  // Note: If you would like the date & time to be seperate columns change the space in the formatting string to a comma - this works because the file type is CSV (Comma Seperated Values)
}

```

## 4/ Références et développement. 
 - [Tutoriel -- Usage d'une horloge DS3231 avec Arduino](https://passionelectronique.fr/tutorial-ds3231/)
 - [Le programme est inspiré de celui proposé par l'Open CTD (License MIT pour Oceanography for everyone)](https://github.com/OceanographyforEveryone/OpenCTD/tree/main)

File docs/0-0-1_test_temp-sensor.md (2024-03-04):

# 0-0-1 -- Test du capteur de température

## 1/ Introduction

Le capteur de [température de blue robotics](https://bluerobotics.com/store/sensors-cameras/sensors/celsius-sensor-r1/) a une précision de 0,1°C et doit être impérativement utilisé avec une tension de 3,3v. 
Dans le cas d'un usage prévu avec une arduino, Blue robotics, recommande d'utiliser un [convertisseur de niveau I2C](https://bluerobotics.com/store/comm-control-power/tether-interface/level-converter-r1/). 

Photo du capteur de température</br>
*Image : © [blue robotics](https://bluerobotics.com/)*

Comme tout câblage I2C, celui-ci contient 4 fils. 
 - Rouge : Vin (3,3v)
 - Noir : GND
 - Blanc: SDA (data)
 - Vert : SCL (clock)

Shéma de broches du câble du capteur de température</br>
*Image : © [blue robotics](https://bluerobotics.com/)*

## 2/ Matériel et fournitures
### 2.1 Fournitures
 - Adafruit adalogger M0 ;
 - [Capteur de température de blue robotics](https://bluerobotics.com/store/sensors-cameras/sensors/celsius-sensor-r1/) ;
 - 2 résistances de 10kΩ ; 
 - Fils de prototypages Arduino ;
 - Plaque de prototypage ; 

### 2.2 Matériel
 - PC sur windows (de préférence) ou linux
 - Logiciel [Arduino IDE](https://www.arduino.cc/en/software)

## 3/ Réalisation
### 3.1 Hardware
Pour réaliser le test de fonctionnement du capteur de température, j'ai utilisé : 
 - Adafruit adalogger M0
 - Platine de prototypage
 - 2 résistances 10kΩ
 - Le capteur de température I2C

Réaliser les branchements suivants. On pourra sectionner le connecteur du capteur de température pour utiliser les fils dénudés. 
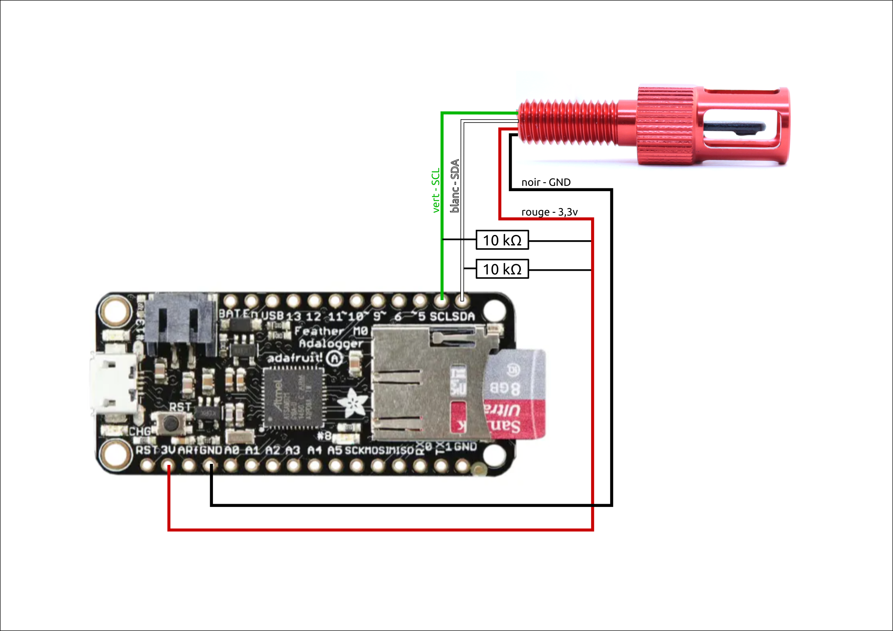
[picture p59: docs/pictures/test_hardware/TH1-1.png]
Shéma de broches du câble du capteur de température
</br>

### 3.2 Software
J'ai réalisé le premier test au moyen du programme proposé par [la documentation de blue robotics](https://bluerobotics.com/learn/celsius-temperature-sensor-installation-and-example-code/). 
 - Télécharger et installer la [librairie Arduino TSYS01](https://github.com/bluerobotics/BlueRobotics_TSYS01_Library)
 - La [la documentation de blue robotics](https://bluerobotics.com/learn/celsius-temperature-sensor-installation-and-example-code/) indique d'utiliser [convertisseur de niveau I2C](https://bluerobotics.com/store/comm-control-power/tether-interface/level-converter-r1/). Dans le cas d'usage d'une adafruit M0 dont l'I2C est en 3,3v, il est possible de faire le branchement en directe. 
 - Brancher la carte adafruit M0 sur l'ordinateur au moyen d'un câble USB. 
 - Lancer votre logiciel Arduino IDE et copier coller ce programme : 
```c++
#include <Wire.h>
#include "TSYS01.h"

TSYS01 sensor;

void setup() {

  Serial.begin(9600);
  
  Serial.println("Starting");
  
  Wire.begin();

  sensor.init();

}

void loop() {

  sensor.read();
 
  Serial.print("Temperature: ");
  Serial.print(sensor.temperature()); 
  Serial.println(" deg C");
   
  Serial.println("&#8212;");

  delay(1000);
}
```

 - Téléverser le programme en sélectionnant :
 	- Le port comm correspondant à la carte branché sur USB ; 
 	- Le bon type de carte ; 
 
 - Ouvrir le moniteur série en sélectionnant "9600". 
 - Ce dernier devrai renvoyer quelque chose comme : 

```
Starting
Temperature: 19.06 deg C
&#8212;
Temperature: 19.07 deg C
&#8212;
Temperature: 19.07 deg C
&#8212;
```

## 4/ Références et développement. 
### 4.1 La valeur de la température était remplacé par "ovf"
 - La mention "ovf" veut dire "overflow", la chaine de caractére est trop longue.
 - Dans mon cas, il s'agissait des connectiques JST qui étaient défectueuses. J'ai donc refais la connectique du capteur entièrement.

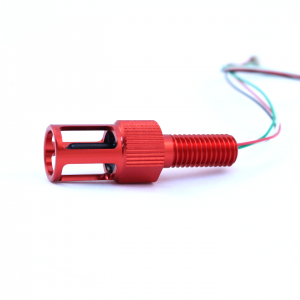
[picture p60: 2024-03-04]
docs/pictures/test_hardware/TH1-2.png

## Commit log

2023-11-28 Premier commit
    [0-1-0_Montage_elec.fzz, Anneau_oeilleton.stl, Dev_Mot_et_RTC.fzz, Dev_mot_rtc_photoR.fzz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]
2023-11-28 mise à jour doc sourcing
    [enregistreur_temperature.ods]
2024-01-16 mise à jour sphinx 0.3.2
    [enregistreur_temperature.ods]
2024-01-20 Correction valise avec mousse
    [enregistreur_temperature.ods]
2024-01-27 MAJ Tableur sourcing
    [enregistreur_temperature.ods]
2024-02-28 doc assemblage préparations et soudures
2024-03-04 001 test sensor temp
2024-05-02 Cablage dans assemblage
2024-05-15 avancement doc assemblage
    [0-1-0_Montage_elec.fzz, Anneau_oeilleton.stl, Bague_bas.stl, Bague_bas_carte.stl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]
